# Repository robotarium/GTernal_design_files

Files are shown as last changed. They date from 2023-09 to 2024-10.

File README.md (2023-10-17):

# GTernal

If looking to purchase circuit boards, this link may hold an up to date CircuitHub order: https://circuithub.com/projects/Payday02/GTernal/revisions/51452/parts

Link to slightly older version with more testing: https://circuithub.com/projects/Payday02/Gritsbot-3/revisions/50001/parts

If looking for a BOM, it can be found in the Parts Folder or here on google sheets (Google sheets may likely be more up to date than the parts folder as parts go in and out of circulation) https://docs.google.com/spreadsheets/d/1fcbRilmKaX-AO9ylUm2N9gINN3ZsyIf4CjUE0T1iR2c/edit?usp=sharing

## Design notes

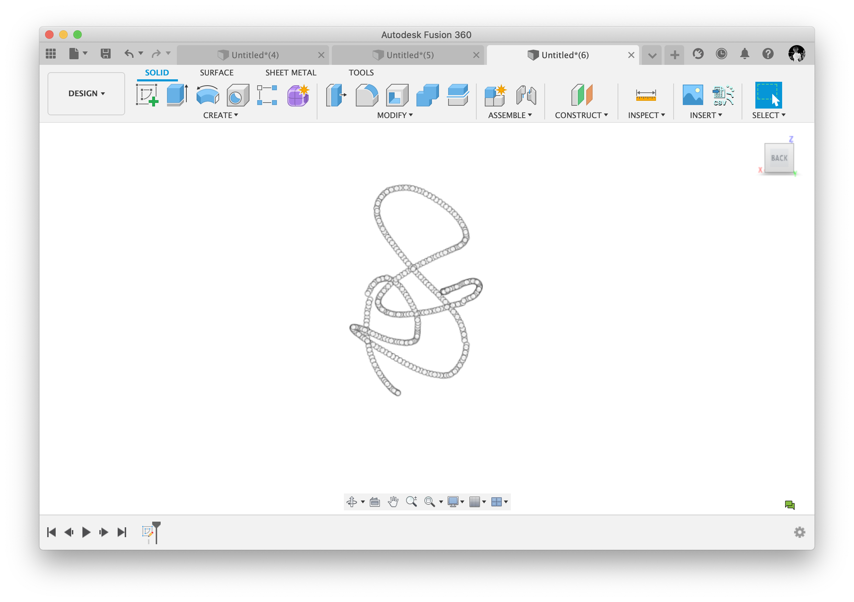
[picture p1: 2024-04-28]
Lasercutting_Files/GTernal_Top_Plates/ImportCSVPoints/images/sketcher_vr_Simple_back.png

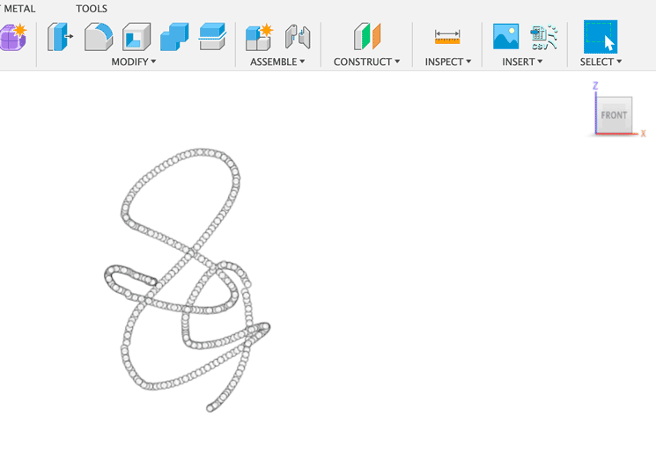
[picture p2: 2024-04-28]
Lasercutting_Files/GTernal_Top_Plates/ImportCSVPoints/images/sketcher_vr_Simple_anim.gif

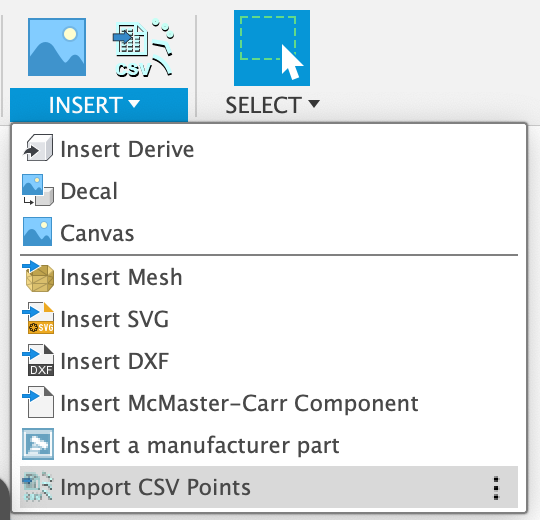
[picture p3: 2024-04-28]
Lasercutting_Files/GTernal_Top_Plates/ImportCSVPoints/images/insert-dropdown.png

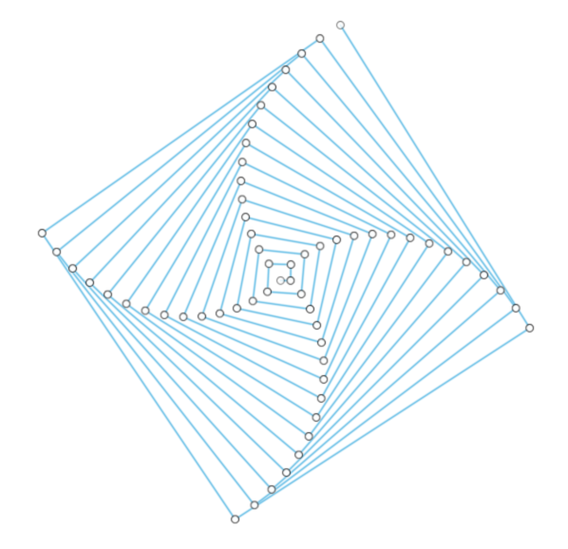
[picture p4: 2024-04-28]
Lasercutting_Files/GTernal_Top_Plates/ImportCSVPoints/images/spiralcube_sketch.png

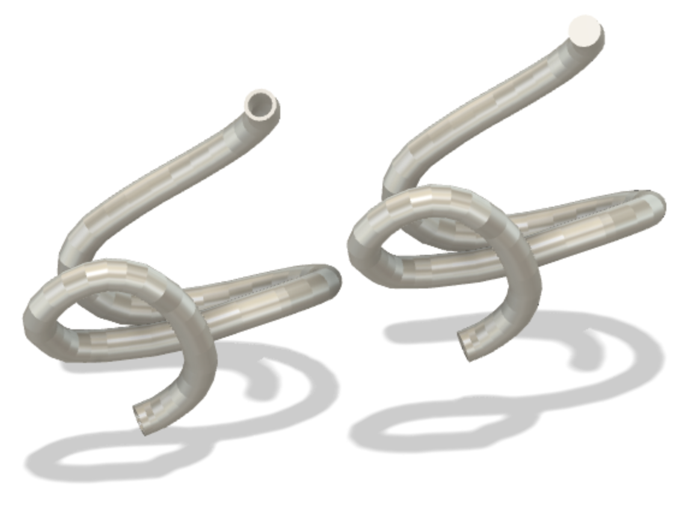
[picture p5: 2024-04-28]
Lasercutting_Files/GTernal_Top_Plates/ImportCSVPoints/images/sketcher_vr_Simple_pipes.png

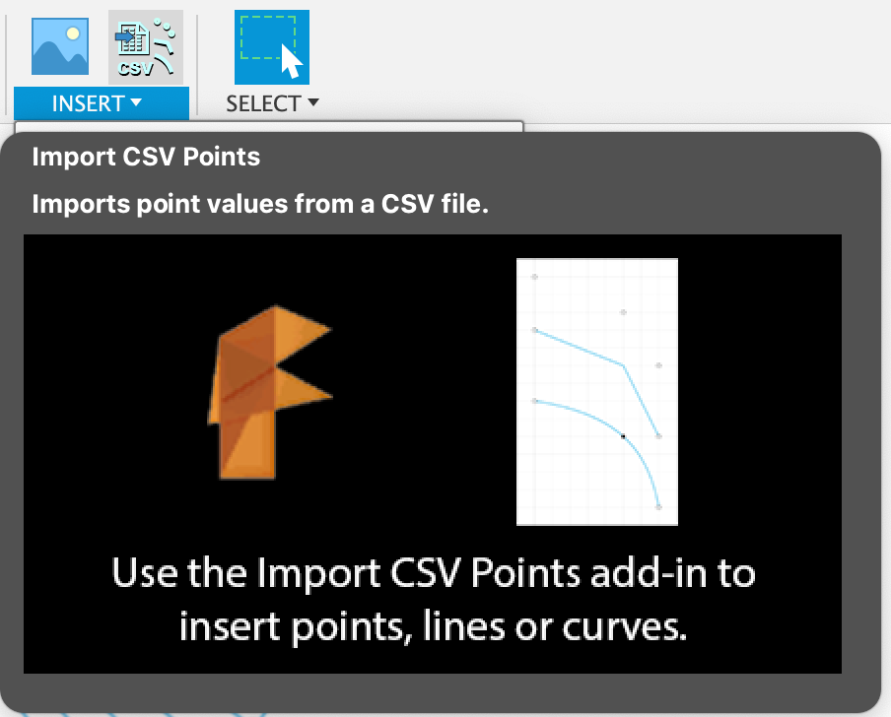
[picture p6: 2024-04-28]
Lasercutting_Files/GTernal_Top_Plates/ImportCSVPoints/images/insert-tooltip.png

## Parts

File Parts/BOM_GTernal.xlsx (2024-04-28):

Name | Link: | Quantity: | Price | Subtotal: | Use/Notes: | Parts Utilization Ratio
Nylon Standoffs (M2.5) | https://a.co/d/cnISycu | 11 | $14.99 | $164.89 | Only using 6 mm, 8 mm, and 20 mm. Pack comes with 15 of each and 4 of each are used per robot. | 0.9696969697
Qi Charger | https://a.co/d/bVD1k2u | 40 | $9.99 | $399.60 |  | 1
Micro SD Card (32 GB) | https://www.amazon.com/dp/B087JCL881/ref=twister_B08CLNX58K?_encoding=UTF8&th=1 | 20 | $15.89 | $317.80 | Pack of 2. 1 needed per robot | 1
Raspberry Pi Camera V2 | https://a.co/d/fKN2s0y | 40 | $19.99 | $799.60 |  | 1
Brass Standoffs (M2.5x15mm) | https://www.digikey.com/en/products/detail/assmann-wsw-components/V6622E/3511510 | 160 | $0.21 | $34.26 | 4 needed per robot | 1
Brass Standoffs (M2.5x10mm) | https://www.digikey.com/en/products/detail/assmann-wsw-components/V6622C/3511505 | 160 | $0.19 | $30.06 | 4 needed per robot | 1
M2.5x6mm Screw | https://www.mcmaster.com/90116A110/ | 2 | $11.10 | $22.20 | 4 Used per robot, pack of 100 | 0.8
Standoff Locknuts (M2.5) | https://www.mcmaster.com/93625A103/ | 7 | $7.00 | $49.00 | 4 Used per robot, pack of 25 | 0.9142857143
24"x24"x1/8" Acrylic sheet | https://www.mcmaster.com/product/8560K194 | 8 | $25.38 | $203.04 | Body Panels. About 5 robots per pannel | 1
12"x12"x1/16" Acrylic sheet | https://www.mcmaster.com/8560K171/ | 8 | $16.88 | $135.04 | Body Panels. About 5 robots per pannel | 1
M2.5x8mm Nylon Screws | https://www.mcmaster.com/92492A712-92492A658/ | 13 | $9.09 | $118.17 | Pack of 100. Distance sensors and Raspberry Pi Mounting. 32 screws per robot. | 0.9846153846
M2.5 Nuts | https://www.mcmaster.com/93800A350-93369A114/?s=m2.5+nylon+nut | 13 | $17.84 | $231.92 | Pack of 100. Distance sensors and Raspberry Pi Mounting. 32 screws per robot. | 0.9846153846
Caster Screws (M3x20mm) | https://www.mcmaster.com/92005A128/ | 2 | $5.14 | $10.28 | Pack of 100. 3 needed per robot | 0.6
Caster Lock Nuts (M3) | https://www.mcmaster.com/90576A102/ | 2 | $4.65 | $9.30 | Pack of 100. 3 needed per robot | 0.6
Pi Cam Screws (M2) | https://www.mcmaster.com/92492A704-92492A104/ | 2 | $13.77 | $27.54 | Pack of 100. 4 needed per robot. | 0.8
Pi Cam Nuts (M2) | https://www.mcmaster.com/93800A300/ | 2 | $20.13 | $40.26 | Pack of 100. 4 needed per robot. | 0.8
Vicon Marker Screws (4-40 1/2") | https://www.mcmaster.com/91772A110/ | 100 | $6.41 | $6.41 | Pack of 100 | NA
Vicon Marker Screws (4-40 3/4") | https://www.mcmaster.com/91772A113/ | 100 | $7.12 | $7.12 | Pack of 100 | NA
Vicon Marker Screws (4-40 1") | https://www.mcmaster.com/91772A115/ | 100 | $7.62 | $7.62 | Pack of 100 | NA
Vicon Marker Screws (4-40 1-1/4") | https://www.mcmaster.com/91772A116/ | 100 | $9.46 | $9.46 | Pack of 100 | NA
Vicon Marker Lock Nuts (4-40) | https://www.mcmaster.com/91831A005/ | 4 | $5.26 | $21.04 | Pack of 100 | NA
Raspberry Pi 4B (2GB) | https://www.sparkfun.com/products/15446 | 40 | 45 | 1800 |  | 1
JST 5-pin Connector | https://www.adafruit.com/product/4875 | 40 | $0.95 | $38.00 | Connector for PCB and RPi | 1
3.7v lipo Battery | https://www.adafruit.com/product/328 | 40 | $14.95 | $598.00 |  | 1
Distance Sensors | https://www.adafruit.com/product/5396 | 280 | $11.96 | $3348.80 | 7 Per robot | 1
Male Pin Header | https://www.adafruit.com/product/392 | 4 | $4.46 | $17.84 | Pack of 10 | 1
100:1 6v motor with encoder | https://www.digikey.com/en/products/detail/dfrobot/FIT0483/7087160?gad_source=1 | 80 | $11.50 | $920.00 | 2 Per robot | 1
Motor mount | https://www.digikey.com/en/products/detail/pololu-corporation/989/10449800 | 40 | $2.95 | $118.00 | Pack of 2. 2 needed per robot | 1
Wheel | https://www.digikey.com/en/products/detail/pololu-corporation/1087/10449804 | 40 | $3.95 | $158.00 | Pack of 2. 2 needed per robot | 1
Ball Caster | https://www.tamiyausa.com/shop/educational-construction/ball-caster-2pcs/ | 20 | $7 | $140.00 | Pack of 2. 1 needed per robot | 1
Caster Springs | https://www.mcmaster.com/9657K601/ | 10 | $6.93 | $69.30 | Pack of 12. 3 needed per robot | 1
Qwiic Cables Short | https://www.sparkfun.com/products/17260 | 280 | $0.95 | $266.00 | 7 needed per robot | 1
Teensy 4.0 | https://www.adafruit.com/product/4323 | 40 | $23.80 | $952.00 |  | 1
PCB | https://circuithub.com/projects/Payday02/GTernal/revisions/51452/parts | 40 | $123.87 | $4954.60 |  | 1
 |  |  | Total: | $16025.15
 | Number of Robots: | 40 | Total with 9% Tax: | $17467.41
 |  |  | Per Robot | $400.63
 |  |  | Per Robot w/ Tax | $436.69

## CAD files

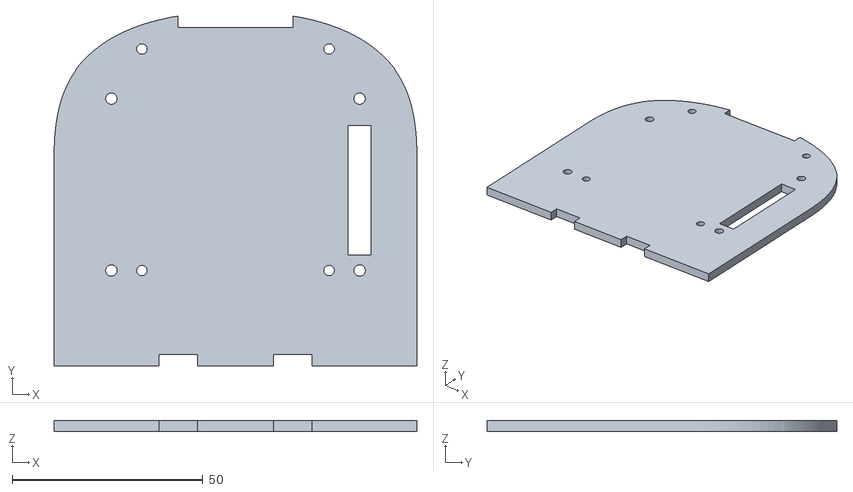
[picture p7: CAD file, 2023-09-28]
CAD_Files/OBJ Files/Top Main Plate.obj
95.0 x 91.6 x 3.00

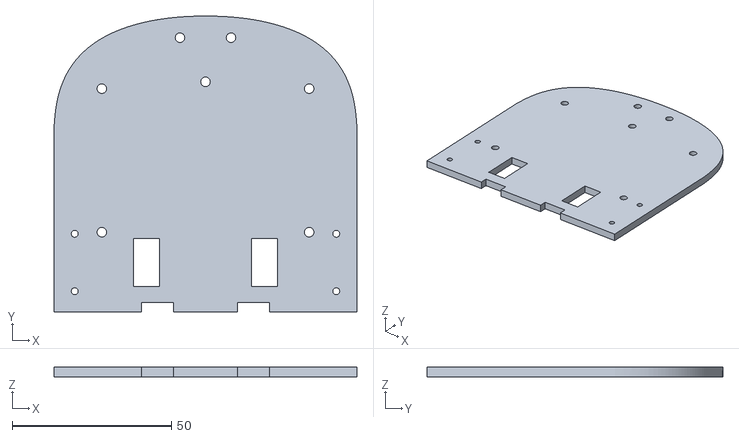
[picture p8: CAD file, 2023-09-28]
CAD_Files/OBJ Files/Bottom Panel.obj
95.0 x 92.8 x 3.00

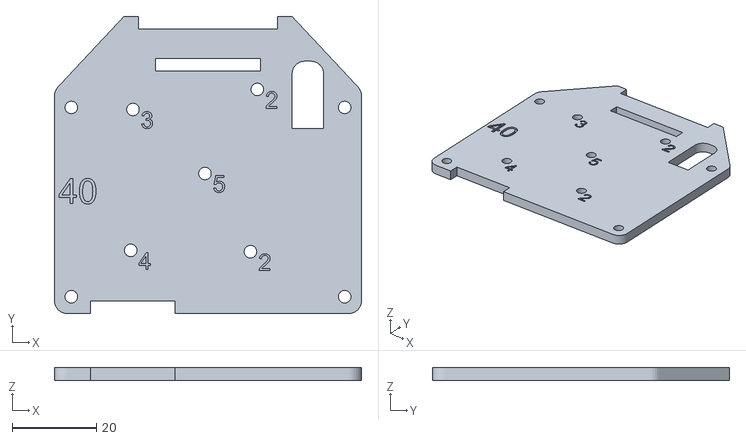
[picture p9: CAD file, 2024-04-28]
Lasercutting_Files/GTernal_Top_Plates/1-40 Objs/Body40.obj
73.0 x 70.6 x 3.00

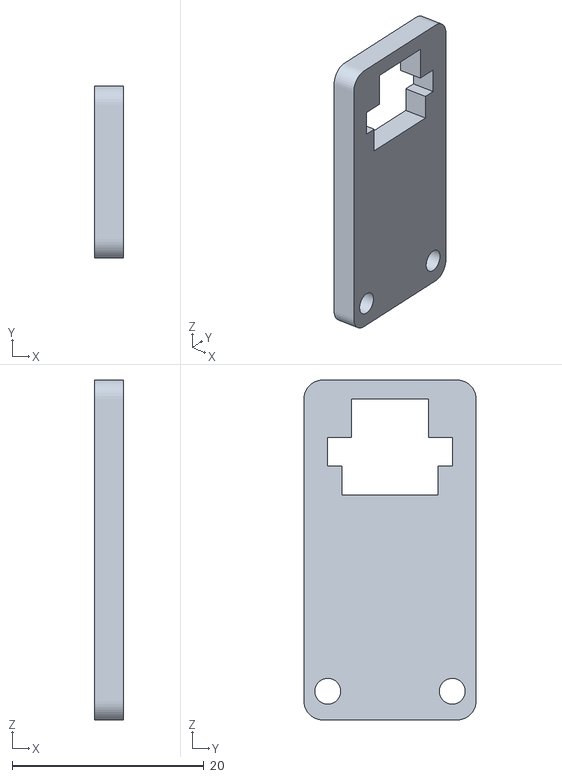
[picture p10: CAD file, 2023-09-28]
CAD_Files/OBJ Files/Distance Sensor Mount Subtractive Part 2 V5.obj
3.00 x 18.0 x 35.5

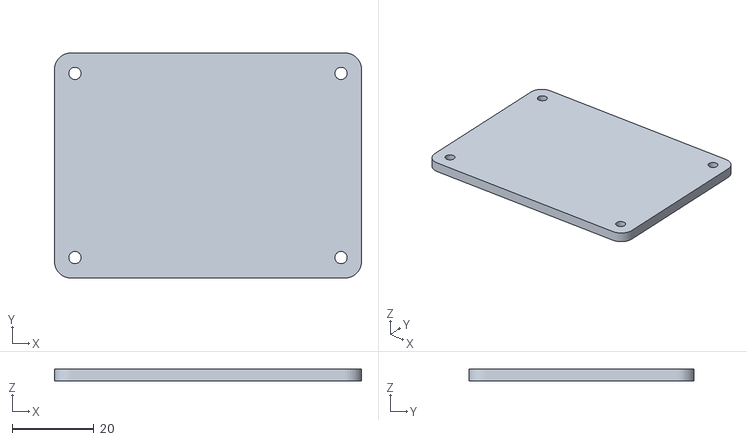
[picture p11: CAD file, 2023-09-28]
CAD_Files/OBJ Files/Battery Plate.obj
75.0 x 55.0 x 3.00

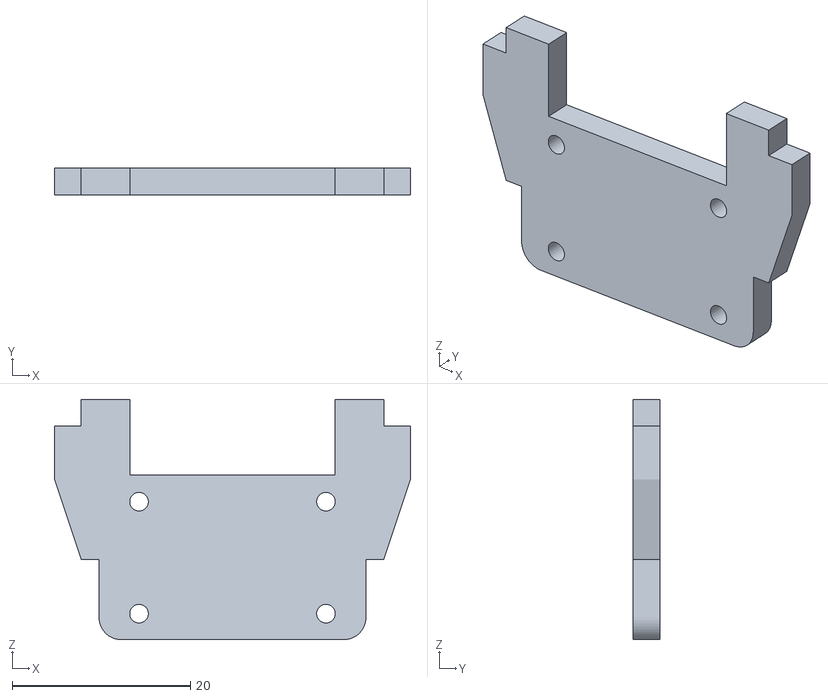
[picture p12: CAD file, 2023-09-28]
CAD_Files/OBJ Files/Camera Mount V3.obj
40.0 x 3.00 x 27.0

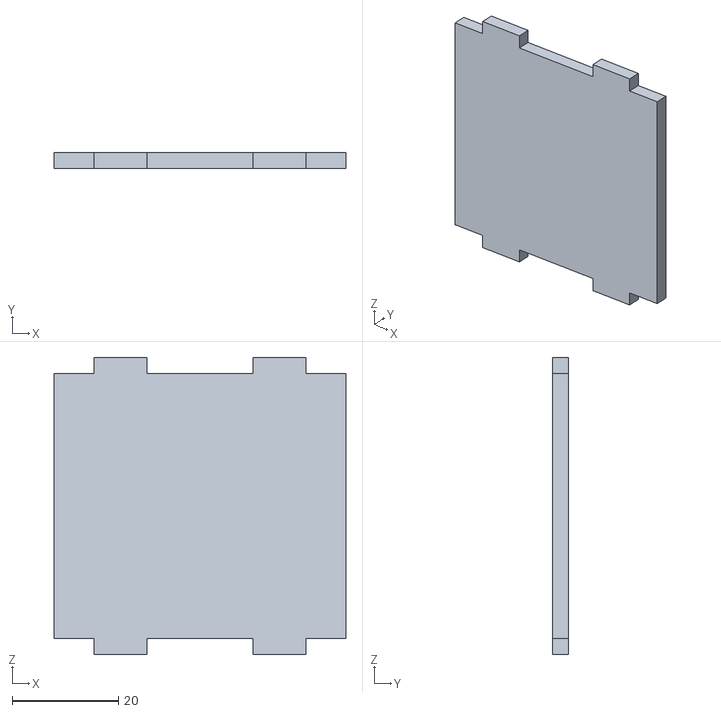
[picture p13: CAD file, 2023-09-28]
CAD_Files/OBJ Files/Back Panel 3mm.obj
55.0 x 3.00 x 56.0

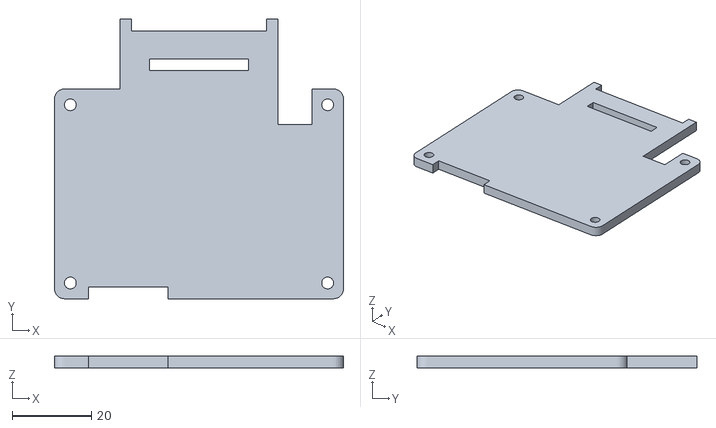
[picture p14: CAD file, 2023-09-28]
CAD_Files/OBJ Files/Top Plate V2.obj
73.0 x 70.6 x 3.00

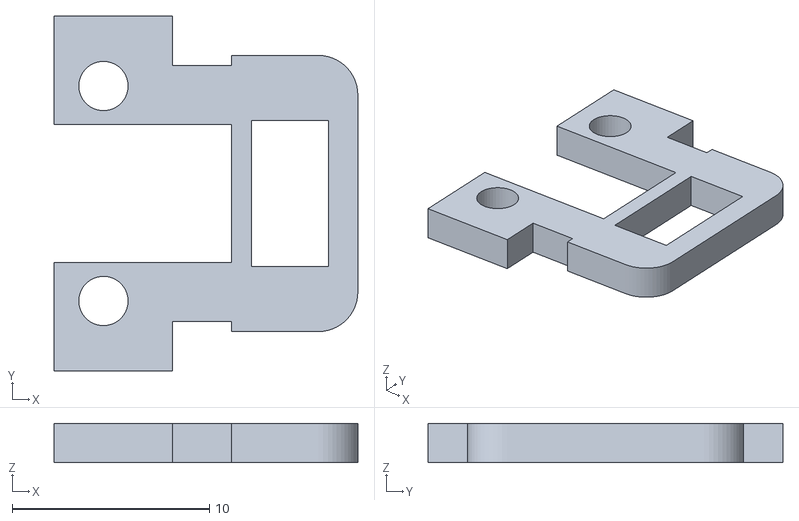
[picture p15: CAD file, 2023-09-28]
CAD_Files/OBJ Files/Distance Sensor mount sub part 1 V1.obj
15.4 x 18.0 x 2.00

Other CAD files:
Lasercutting_Files/GTernal_Top_Plates/1-40 Objs/Body22.obj
Lasercutting_Files/GTernal_Top_Plates/1-40 Objs/Body14.obj
Lasercutting_Files/GTernal_Top_Plates/1-40 Objs/Body2.obj
Lasercutting_Files/GTernal_Top_Plates/1-40 Objs/Body25.obj
Lasercutting_Files/GTernal_Top_Plates/1-40 Objs/Body1.obj
Lasercutting_Files/GTernal_Top_Plates/1-40 Objs/Body20.obj
Lasercutting_Files/GTernal_Top_Plates/1-40 Objs/Body28.obj
Lasercutting_Files/GTernal_Top_Plates/1-40 Objs/Body34.obj
Lasercutting_Files/GTernal_Top_Plates/1-40 Objs/Body19.obj
CAD_Files/Components/EDAC_1743_RJ45_TH.f3d
CAD_Files/Components/Pin+Header+2x2+TH+Pitch+2.f3d
CAD_Files/Components/SMD+PTC+Fuse+MF-MSMF250_16X.f3d
CAD_Files/Components/SOP-3+2.f3d
CAD_Files/Components/SOP-3.f3d
CAD_Files/Components/TSOP-2+4mm.f3d
CAD_Files/Components/TSOP-6+2mm.f3d
CAD_Files/Components/TSOP-6+3mm (1).f3d
CAD_Files/Components/TSOP-6+3mm.f3d
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

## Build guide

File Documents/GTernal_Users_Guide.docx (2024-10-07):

GTernal 1.1

User’s Guide

Paden Davis, Maxwell Chen, Nathan Yam,

Soobum Kim, Sean Wilson, Samuel Coogan

October, 2024

Table of Contents

# 1 Purpose

The purpose of this document is to explain the general design elements, assembly, and usage of the GTernal 1.1 robot.

# 2 Printed Circuit Board (PCB)

The printed circuit board (PCB) houses most of the electronics on the robot and features circuitry for power and sensors. Some of the circuitry is taken from the GRITSBot 2.0 PCB while other components are copied and modified versions of circuitry from breakout boards.

The top side of the PCB includes an On/Off switch, status LEDs, and an area for mounting a Teensy 4.0 microcontroller.

This section will detail the core components of the GTernal 1.0 PCB.

## 2.1 On/Off Switch

The On/Off switch turns on and off the 5V and 6V power circuits of the robot. The On/Off switch has no connection to the charging circuitry.

## 2.2 Status LEDs

Status LED | Description
PWR | On when On/Off switch is on and receiving power from battery/charger
LBO | Low battery indicator
CHRG | On when battery is charging or only charger connected.
DONE | On when batter is done charging.

## 2.3 5V Regulation

The 5V Regulation circuitry is taken and modified from Adafruit’s PowerBoost 1000C board (https://www.adafruit.com/product/2465).

The circuitry takes power from the battery/charger and regulates it to 5V to power the Teensy, motor encoders, and motor driver.

## 2.4 6V Regulation

The 6V Regulation circuitry is taken from the GRITSBot 2.0 PCB.

The circuitry takes power from the battery/charger and regulates it to 6V for motor power.

## 2.5 Charging Circuitry

The charging circuitry is taken and modified from Adafruit’s PowerBoost 1000C board (https://www.adafruit.com/product/2465).

The circuitry handles charging the robot battery and load-sharing between charger and battery.

## 2.6 Power Sensor

The power monitor is taken and modified from Adafruit’s INA260 Breakout Board (https://www.adafruit.com/product/4226).

The INA260 power sensor is wired in series with the VBAT line directly after the charging circuitry and measures VBAT voltage/current and power usage.

If undesired, the PCB features pads for a jumper on the VBAT line to bypass the power sensor.

## 2.7 Teensy 4.0

The Teensy 4.0 (https://www.pjrc.com/store/teensy40.html) is a low-level microcontroller board that handles sensor and motor driver communications and control.

The Teensy takes in 5V and provides 3.3V for sensor power. The Teensy can be connected to microUSB for programming.

WARNING: There is potential for damage to the 5V regulation circuitry if the Teensy is connected to microUSB without battery/charger power. The cause is unknown at the moment but may be due to pre-biasing the output of the TPS61030 chip. Ensure that the robot is fully powered through battery/charger first before connecting the Teensy with microUSB that has external power.

## 2.8 H-Bridge Motor Driver

The H-Bridge Motor Driver takes power from 5V regulation and uses 6V for motor power. The driver is controlled by the Teensy.

## 2.9 I²C Mux and Qwiic Connectors

The I²C is taken and modified from Sparkfun’s Qwiic Mux Breakout (https://www.sparkfun.com/products/16784).

The GTernal 1.0 features seven distance sensors (https://www.adafruit.com/product/3317) with the same, unmodifiable I²C address, so I²C mux circuitry is needed to properly access all of them.

The GTernal 1.0 PCB includes Qwiic connectors for wiring to the distance sensors and holes for distance sensor mounts.

## 2.10 Inertial Measurement Unit (IMU)

The I²C is taken and modified from Adafruit’s BNO055 Breakout Board (https://www.adafruit.com/product/2472).

## 2.10 Pi Power & Communication

The PCB features 4 pins for providing power and serial communication to a Raspberry Pi.

# 3 Other Electronics and Components

This section details other electronics and components not on the PCB.

## 3.1 Distance Sensors

The GTernal 1.0 features seven Adafruit VL53L0X Time of Flight Distance Sensors (https://www.adafruit.com/product/3317).

These distance sensors are connected to the PCB through a Qwiic cable and should be held using 3D-printed or laser-cut mounts that can be bolted to the PCB.

## 3.2 Raspberry Pi

The GTernal 1.0 supports Raspberry Pi 3, 3b, 3b+, and 4.

The Raspberry Pi receives power from the Pi power pins on the PCB.

The Raspberry Pi serves as the main processor for the robot and communicates with the Teensy either through serial pins on the PCB or through USB

## 3.3 Pi Camera

The intended camera is a Raspberry Pi Camera V2 (https://www.raspberrypi.com/products/camera-module-v2/), but the GTernal 1.1 should support any camera that connects to a Raspberry Pi through the CSI connector.

## 3.4 Motors

The GTernal 1.0 uses two geared motors with encoders from DFRobot (https://www.dfrobot.com/product-1433.html).

## 3.5 Battery

The GTernal 1.0 uses a 3.7V LiPo Battery from Adafruit (https://www.adafruit.com/product/328)

# 4 Assembly

This section’s purpose is to walk through the steps involved in putting together a working robot once all of the parts have been purchased or manufactured. To this end, the assembly process will require:

- 1x GTernal 1.0 assembled printed circuit board (PCB)
- 1x Set of cut acrylic pieces (see 4.1)
  - Bottom plate
  - Pi mount plate
  - Top plate
  - Battery plates
  - 2x Back plates
  - 7x Distance sensor mount plates
  - Camera mount plate
- 1x 3.7V LiPo Battery
- 1x Teensy 4.0 board with pins soldered
- 1x Raspberry Pi (3B, 3B+, 4)
- 1x JST SH Jumper Wire
- 7x Time of Flight (ToF) distance sensors
- 7x 50mm or shorter Qwiic connector cables
- 1x Front Caster Pack
- 3x Small Caster Springs
- 3x M3x20mm Screws
- 3x M3 Locknuts
- 2x 100:1 Motors
- 1x Pack of two motor mounts
- 1x Pack of two wheels
- 4x M2.5x15mm brass male to female standoffs
- 4x M2.5x10mm brass male to female standoffs
- 4x M2.5x6mm nylon male to female standoffs
- 4x M2.5x10mm nylon male to female standoffs
- 4x M2.5x20mm nylon male to female standoffs
- 4x M2.5 Locknuts
- 4x M2.5x6mm Screws
- 14x M2 nylon Screws
- 14x M2 nylon Nuts

## 4.1 Cut Acrylic Pieces

.svg and .pdf files for laser cutting acrylic pieces can be found in the GTernal GitHub repository under “GTernal/Lasercutting Files”.

Piece label is given inside square brackets.

Images in this section are not to scale.

### 4.1.1 Bottom Plate [A1]

Thickness: 1/8” (3 mm)

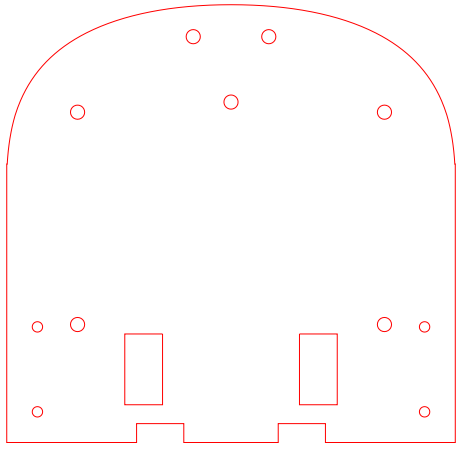
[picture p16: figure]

### 4.1.2 Pi Mount Plate [A2]

Thickness: 1/8” (3 mm)

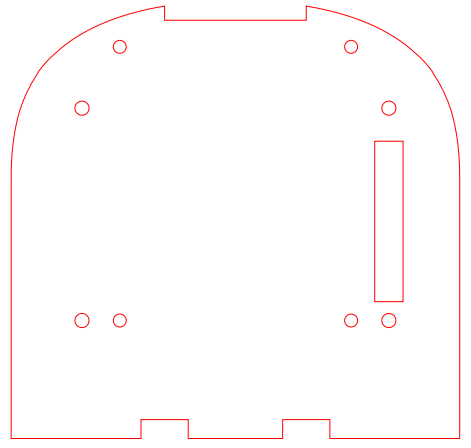
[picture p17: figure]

### 4.1.3 Top Plate [A3]

Thickness: 1/16” (1.5 mm)
Left: base top plate.
Right: example top plate with holes for mounting Vicon trackers

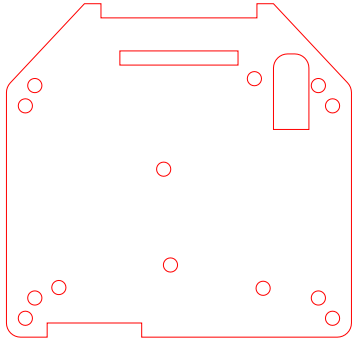
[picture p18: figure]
A red outline of a machine

### 4.1.4 Battery Plates [A4b, A4t]

Bottom Plate [A4b] Thickness: 1/8” (3 mm)

Top Plate [A4t] Thickness: 1/16” (1.5 mm)

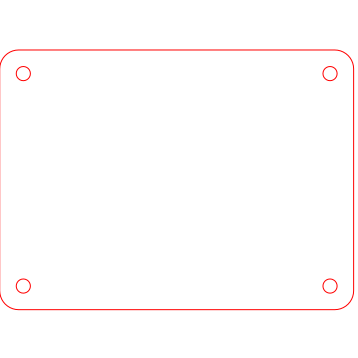
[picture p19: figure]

### 4.1.5 Back Plates [A5]

Thickness: 1/16” (1.5 mm)

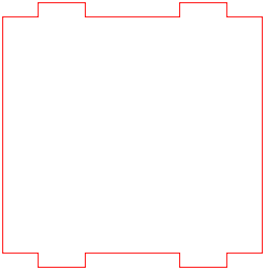
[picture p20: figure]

### 4.1.6 Distance Sensor Mount Plates [A6a, A6b]

Thickness: 1/8” (3 mm)

Number: 7x

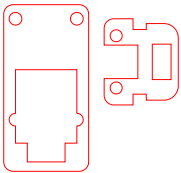
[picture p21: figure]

### 4.1.7 Camera Mount Plate [A7]

Thickness: 1/8” (3 mm)

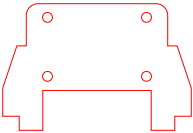
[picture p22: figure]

## 4.2 Assembly with an Assembled Circuit Board

For this process, the steps are much simpler than without a circuit board (PCB), as all connections except the motor connections will involve no soldering.

1. Mount the teensy onto the top of the PCB by putting the pins through the holes in the marked section on the silkscreen then soldering the pins to the PCB.
2. Solder the motor connectors that come with each motor into the holes marked motorR and motorL respectively. Review pinouts for the motor, motor cable, and PCB to ensure correct connection.
3. The distance sensor mounts are made of two acrylic plates [A6a] and [A6b].
  i. Take the smaller plate [A6b] and insert it diagonally through the center hole of the larger plate [A6a].
  ii. Rotate and shift [A6b] until it snaps into place horizontally near the edge of plate [A6a].

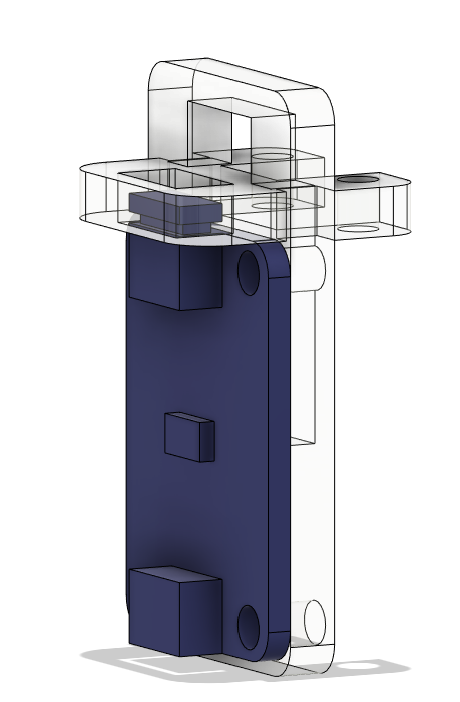
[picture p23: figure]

4. Repeat step (3) six more times to obtain seven total distance sensor mounts.
5. Mounting a distance sensor onto a distance sensor mount.
  i. Take a 50mm or shorter Qwiic connector cable and plug it into the connector on the side with the LED. When facing distance sensor with top silkscreen text upright, this is the left connector.
  ii. Thread the Qwiic connector cable through the upper donut hole in piece A6a in the distance sensor mount.
  iii. With the cable through the hole, align the right-side distance sensor holes with the bottom holes on the larger plate [A6a] of the distance sensor mount.
  iv. Secure the distance sensor using 2x M2x8mm nylon screws and 2x M2 nylon nuts on the bottom holes of the distance sensor mount.
6. Repeat step (5) six more times to obtain seven total mounted distance sensors with Qwiic jumpers out the back of the mount.
7. Mounting distance sensors to PCB
  i. With the Qwiic connector cable plugged into the distance sensor, plug the free connector on the cable into the Qwiic connector on the PCB.
  ii. Using 2x M2x8mm nylon screws and 2x M2 nylon nuts, secure the distance sensor mount into the PCB through the screw holes on acrylic piece [A6b].
8. Repeat step (7) for all seven distance sensors. Set the PCB to the side gently once all seven are mounted.
9. Begin with the bottom acrylic plate [A1]. This one has two rectangular holes near the bottom side and three screw holes in the front. Screw 4 M2.5x10mm brass standoffs into lock nuts through the four rectangularly spaced holes in the plate. Use pliers to hold them while screwing into the locknut if necessary.
10. Place the motors into their mounting brackets, making sure the flat panel at the end of the gearbox lines up with the edge of the bracket. Mount the brackets and motors to the bottom side (opposite side to the standoffs) of the acrylic plate [A1] using the screws provided with the brackets.

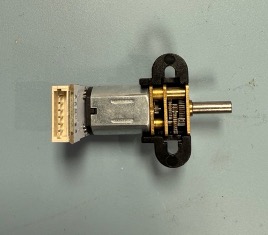
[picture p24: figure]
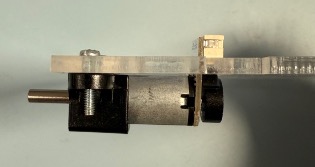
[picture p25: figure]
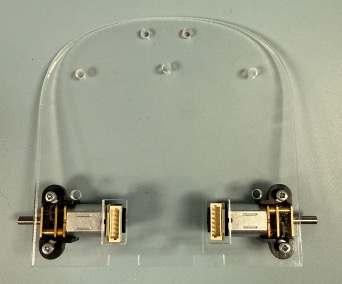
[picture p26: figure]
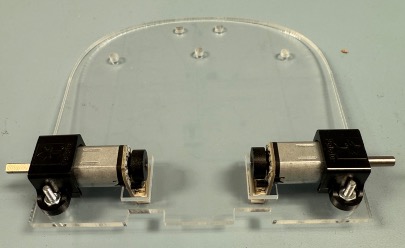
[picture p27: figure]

11. Place the wheels onto the motor shafts and make sure the wheels are angled straight and do not rub against the acrylic. Place the rubber ring on the outside to tighten them and lock them in place.
12. Mounting the caster wheel to the bottom plate [A1].
  i. Clip the caster wheel components out of the injection molded sprue. Set aside the mounting base since it will not be used.
  ii. Place the metal marble in the bottom holder.
  iii. Place three metal pins on top of the ball in each of the edge locations.

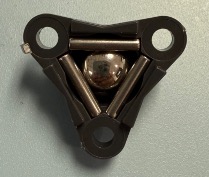
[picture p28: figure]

  iv. Place the top onto the caster assembly.
  v. Thread 3x M3x20mm screws into the three holes on the caster.
  vi. Place the caster springs and the 2mm spacers that come with the casters onto the screws.
  vii. Carefully slot all three screws through the holes in the front of the bottom plate [A1]. Secure the screws in place with 3x M3 Locknuts.

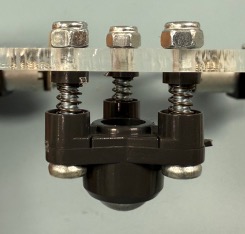
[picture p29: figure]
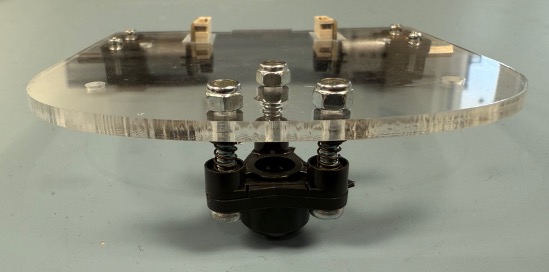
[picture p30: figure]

  viii. Check if the bottom plate is level. Adjust the 3x M3 Locknuts if necessary.

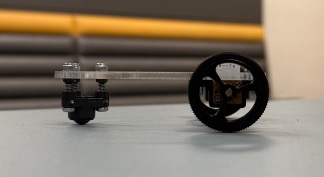
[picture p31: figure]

13. Place the bottom battery plate [A4b] (rectangle with rounded corners) onto the standoffs and attach 4x 10mm nylon standoffs through it into the brass standoffs of the bottom plate [A1] to secure it in place.
14. On top of the bottom battery plate [A4b], place the battery.
15. With the top battery plate [A4t] close, take the battery wires and place them under the plate [A4t] in a way that will hold them and leaves about 2cm of wire free.
16. Press the top battery plate [A4t] down and attach 4x 6mm nylon standoffs to secure it in place.
17. Mounting the PCB
  i. Ensure the power switch is switched off (towards the bottom of the board).
  ii. Bring the PCB with the teensy attached close.
  iii. Route the motor wires under the PCB (careful to go around the teensy pins) and across each other.
  iv. Place the PCB on the standoffs and secure it with 4x 20mm standoffs.
  v. Plug the motor connectors into their corresponding motor
  vi. Plug the battery cable into the battery connector. All lights should be off if the switch is in the off position.
18. Place the JST SH connector into the Pi Communication connector on the PCB
19. Screw the Raspberry Pi onto the Pi mount plate [A2], which looks similar to the bottom plate of the robot, using 4x M2x8mm nylon screws and nuts.
20. Thread the four wires through the slot on the right side of the plate and connect them to pins 2,3,4,5 (5v, GND, Tx, Rx) from the top on the right column of pins in the same order they are on the PCB.
21. Attach the Pi mount plate [A2] to the standoffs from the PCB using 4x M2.5x15mm brass standoffs.
22. If using Vicon Trackers, attach the screws used for the tracking balls into the top plate
23. Securing the top plate [A3]
  i. If using the camera, route the camera cable through the plate and into the connector on the Pi before screwing the plate in
  ii. Screw on the top plate [A3] using 4x M2.5x6mm screws.
24. If using the camera, press fit the camera mount plate into the front slots. Then mount the camera to the camera mount plate.
25. Backplates and Qi Charger
  i. Press fit one back plate [A5] into the grooves
  ii. Plug the Qi Charger into the charging microUSB port on the side of the PCB
  iii. Place the flat side against the back plate [A5] that was mounted in step (25i).
  iv. Place another back plate [A5] into the same grooves, sandwiching the Qi charger between two plates to hold it in place.

# 5 Uploading Code and Using the GTernal 1.0

Upload the Teensy code found in the GitHub Gritsbot3/Firmware/teensyCode folder into the Teensy on the PCB through its microUSB port. Remember to have the board powered on and connected to the battery or charge port before plugging in the Teensy. This will require the Gritsbot3/Library folder to be placed in your Arduino libraries and the Arduino IDE set up to work with Teensy 4.0 which can be done following this guide (https://www.pjrc.com/teensy/td_download.html).

Image the Raspberry Pi SD card with the image provided in the GitHub repository and plug that into the Pi. Power the Pi by turning on the GTernal robot and connect the Pi to a monitor through the HDMI port or USB C port depending on which version you are using. Plug a mouse and keyboard into the rear USB A ports and use this to complete the setup of the Pi and add a Wi-Fi connection. A Wi-Fi antenna can optionally be connected into the rear USB A ports for better signal.

# 6 Future Changes

- Add additional pinout headers to the PCB or a Qwiic header to allow extra I2C connections for breakout boards.
- Mosfet for cutting power to the Pi for charging timeouts
- Move PCB components to improve ground/power connections and heat characteristics.

# 7 Links and References

## 7.1 Bill of Materials

GTernal 1.0 BOM: https://docs.google.com/spreadsheets/d/1fcbRilmKaX-AO9ylUm2N9gINN3ZsyIf4CjUE0T1iR2c/edit?usp=sharing

## 7.2 GitHub

GTernal 1.0: https://github.com/robotarium/GTernal

GRITSBot 2.0 Hardware: https://github.com/robotarium/GRITSBot_hardware_design

## 7.3 Robotarium

Robotarium at Georgia Tech: https://www.robotarium.gatech.edu/

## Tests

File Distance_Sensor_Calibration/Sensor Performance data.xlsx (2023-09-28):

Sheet: Export Summary
This document was exported from Numbers. Each table was converted to an Excel worksheet. All other objects on each Numbers sheet were placed on separate worksheets. Please be aware that formula calculations may differ in Excel.
Numbers Sheet Name | Numbers Table Name | Excel Worksheet Name
20 inches
 | Table 1 | 20 inches
12 inches
 | Table 1 | 12 inches
4 inches
 | Table 1 | 4 inches
3 inches
 | Table 1 | 3 inches
2 inches
 | Table 1 | 2 inches
6 inches
 | Table 1 | 6 inches
8 inches
 | Table 1 | 8 inches
10 inches
 | Table 1 | 10 inches
14 inches
 | Table 1 | 14 inches
16 inches
 | Table 1 | 16 inches
18 inches
 | Table 1 | 18 inches
22 inches
 | Table 1 | 22 inches
24 inches
 | Table 1 | 24 inches
26 inches
 | Table 1 | 26 inches
28 inches
 | Table 1 | 28 inches
Sheet 4
 | Table 1 | Sheet 4
Sheet 1
 | Table 1 | Sheet 1
Graphs
 | Table 1 | Graphs
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

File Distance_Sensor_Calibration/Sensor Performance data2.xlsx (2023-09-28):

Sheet: Export Summary
This document was exported from Numbers. Each table was converted to an Excel worksheet. All other objects on each Numbers sheet were placed on separate worksheets. Please be aware that formula calculations may differ in Excel.
Numbers Sheet Name | Numbers Table Name | Excel Worksheet Name
20 inches
 | Table 1 | 20 inches
12 inches
 | Table 1 | 12 inches
4 inches
 | Table 1 | 4 inches
3 inches
 | Table 1 | 3 inches
2 inches
 | Table 1 | 2 inches
6 inches
 | Table 1 | 6 inches
8 inches
 | Table 1 | 8 inches
10 inches
 | Table 1 | 10 inches
14 inches
 | Table 1 | 14 inches
16 inches
 | Table 1 | 16 inches
18 inches
 | Table 1 | 18 inches
22 inches
 | Table 1 | 22 inches
24 inches
 | Table 1 | 24 inches
26 inches
 | Table 1 | 26 inches
28 inches
 | Table 1 | 28 inches
Graphs
 | Table 1 | Graphs
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

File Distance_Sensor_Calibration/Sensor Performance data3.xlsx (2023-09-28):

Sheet: Export Summary
This document was exported from Numbers. Each table was converted to an Excel worksheet. All other objects on each Numbers sheet were placed on separate worksheets. Please be aware that formula calculations may differ in Excel.
Numbers Sheet Name | Numbers Table Name | Excel Worksheet Name
20 inches
 | Table 1 | 20 inches
12 inches
 | Table 1 | 12 inches
4 inches
 | Table 1 | 4 inches
3 inches
 | Table 1 | 3 inches
2 inches
 | Table 1 | 2 inches
6 inches
 | Table 1 | 6 inches
8 inches
 | Table 1 | 8 inches
10 inches
 | Table 1 | 10 inches
14 inches
 | Table 1 | 14 inches
16 inches
 | Table 1 | 16 inches
18 inches
 | Table 1 | 18 inches
22 inches
 | Table 1 | 22 inches
24 inches
 | Table 1 | 24 inches
26 inches
 | Table 1 | 26 inches
28 inches
 | Table 1 | 28 inches
Graphs
 | Table 1 | Graphs
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

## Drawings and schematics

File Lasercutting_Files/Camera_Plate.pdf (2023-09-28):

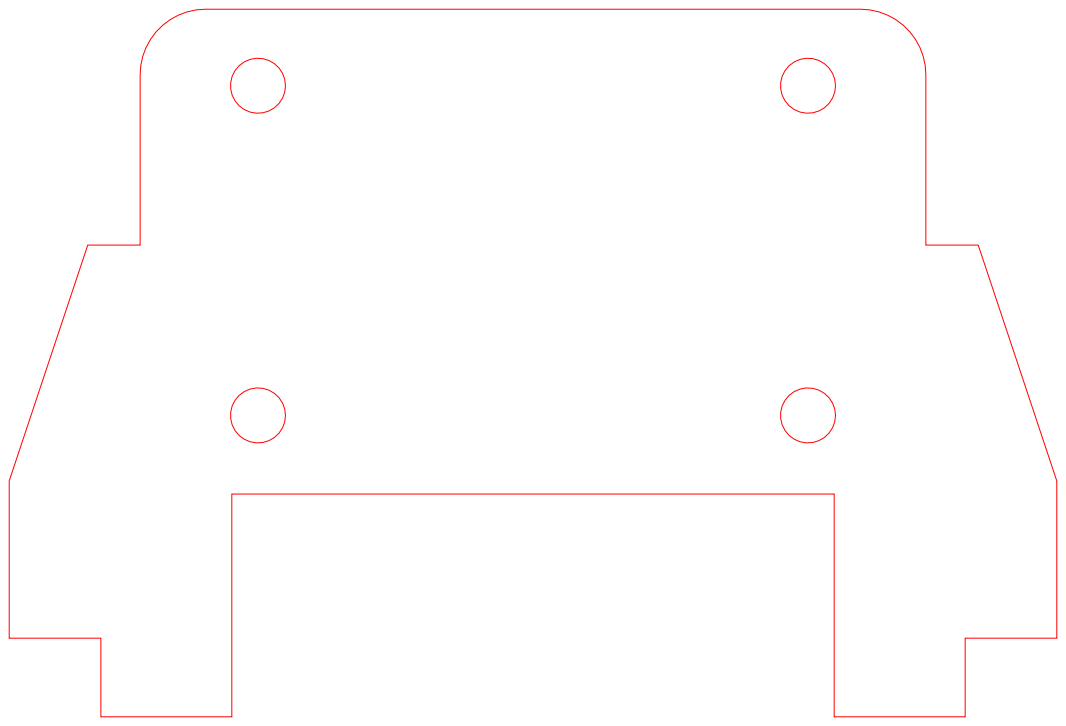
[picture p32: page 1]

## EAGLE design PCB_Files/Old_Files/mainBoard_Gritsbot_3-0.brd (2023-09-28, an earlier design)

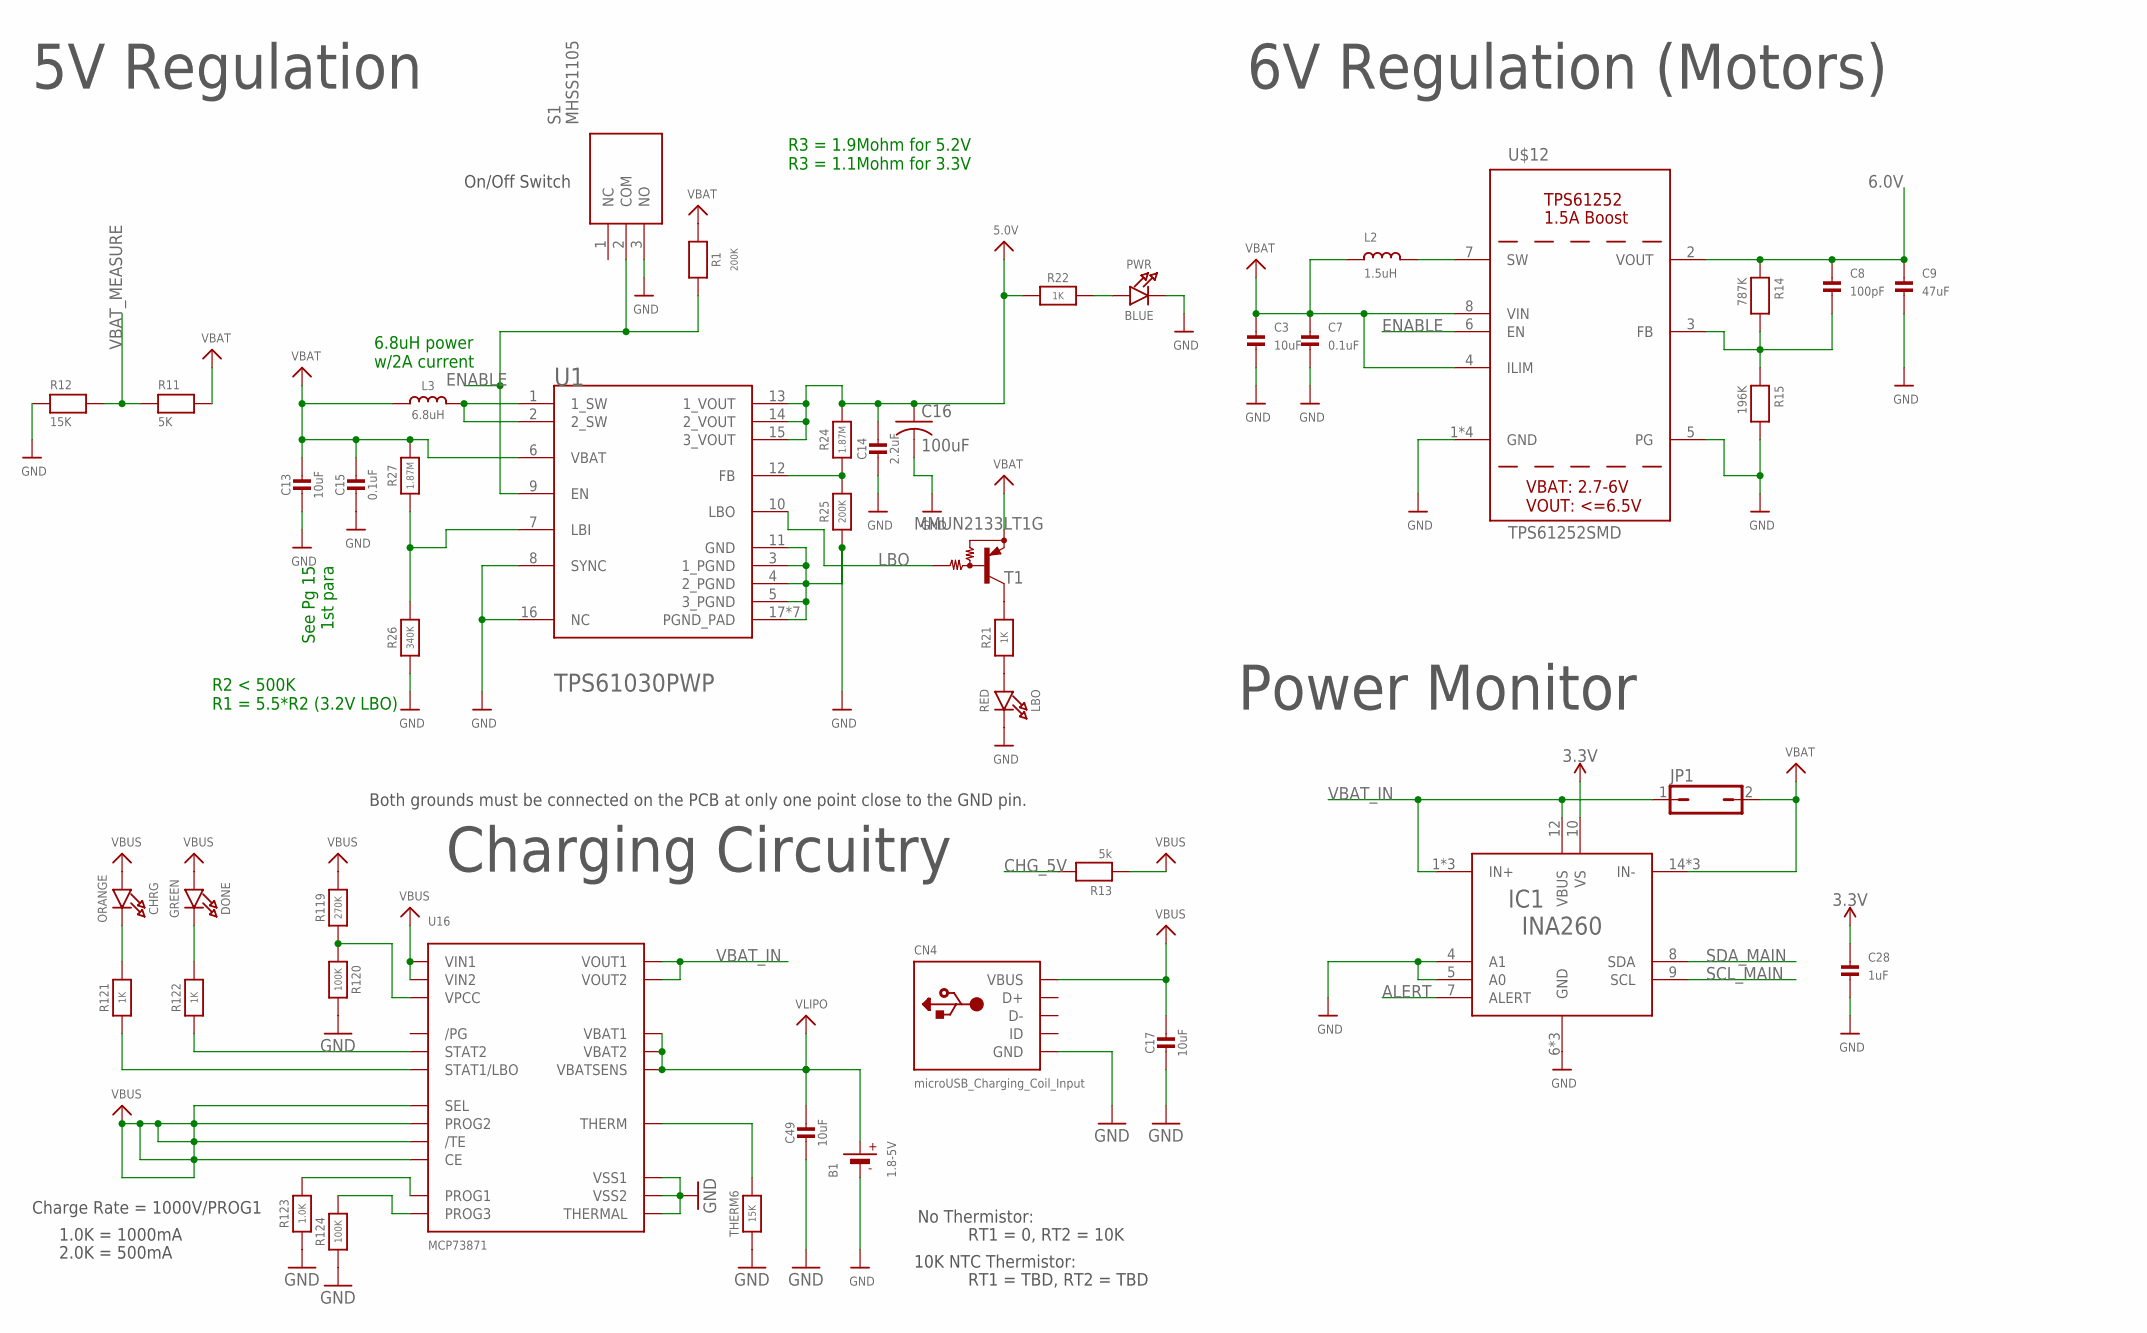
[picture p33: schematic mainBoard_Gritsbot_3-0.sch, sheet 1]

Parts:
B1: 1.8-5V; JSTPH2
C3: 10uF; 0603
C7: 0.1uF; 0805
C8: 100pF; 0603
C9: 47uF; 1206
C13, C17, C49: 10uF; 0805-NO
C14: 2.2uF; 0805-NO
C15: 0.1uF; 0805_10MGAP
C16: 100uF; C1210
C28: 1uF; 0603-NO
CHRG: ORANGE; CHIPLED_0805_NOOUTLINE
CN4: microUSB_Charging_Coil_Input; 4UCONN_20329
DONE: GREEN; CHIPLED_0805_NOOUTLINE
IC1: INA260; TSSOP16
JP1: JP1Q; JP1
L2: 1.5uH; MURATA_DFE252012P-1R5M=P2
L3: 6.8uH; INDUCTOR_5X5MM_TDK_VLC5045
LBO: RED; CHIPLED_0805_NOOUTLINE
PWR: BLUE; CHIPLED_0805_NOOUTLINE
R1, R25: 200K; 0805-NO
R11: 5K; 0805
R12: 15K; 0805
R13: 5k; 0805
R14: 787K; 0805
R15: 196K; 0805
R21, R22, R121, R122: 1K; 0805-NO
R24: 1.87M; 0805-NO
R26: 340K; _0805MP
R27: 1.87M; _0805MP
R119: 270K; 0805-NO
R120, R124: 100K; 0805-NO
R123: 1.0K; 0805-NO
S1: MHSS1105
T1: MMUN2133LT1G; SC59-BEC
THERM6: 15K; 0805-NO
U1: TEXAS_INSTRUMENTS_TPS61030PWPTEXAS_INSTRUMENTS_TP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; TEXAS_INSTRUMENTS_TPS61030PWP_0
U16: MCP73871; QFN20_4MM
U$12: TPS61252SMD; TPS61252

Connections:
3.3V: C28.1, IC1.10 (VS); also elsewhere on the board
5.0V: C14.1, C16.1, R22.1, R24.2, U1.13 (1_VOUT), U1.14 (2_VOUT), U1.15 (3_VOUT); also elsewhere on the board
6.0V: C8.1, C9.1, R14.1, U$12.2 (VOUT); also elsewhere on the board
ALERT: IC1.7 (ALERT)
CHG_5V: R13.2; also elsewhere on the board
ENABLE: R1.2, S1.2 (COM), U1.9 (EN), U$12.6 (EN)
GND: B1.1 (-), C3.2, C7.2, C9.2, C13.2, C14.2, C15.2, C16.2, C17.2, C28.2, C49.2, CN4.BASE@1 (GND), CN4.BASE@2 (GND), CN4.GND, CN4.SPRT@1 (GND), CN4.SPRT@2 (GND), CN4.SPRT@3 (GND), CN4.SPRT@4 (GND), IC1.4 (A1), IC1.5 (A0), IC1.6 (GND), IC1.11 (GND), IC1.13 (GND), LBO.C, PWR.C, R12.1, R15.2, R25.1, R26.1, R120.2, R123.1, R124.1, S1.3 (NO), THERM6.1, U1.3 (1_PGND), U1.4 (2_PGND), U1.5 (3_PGND), U1.8 (SYNC), U1.11 (GND), U1.16 (NC), U1.17 (PGND_PAD), U1.PAD_1 (PGND_PAD), U1.PAD_2 (PGND_PAD), U1.PAD_3 (PGND_PAD), U1.PAD_4 (PGND_PAD), U1.PAD_5 (PGND_PAD), U1.PAD_6 (PGND_PAD), U16.P$10 (VSS1), U16.P$11 (VSS2), U16.P$21 (THERMAL), U$12.1 (GND), U$12.5 (PG), U$12.P$2_GND (GND), U$12.P$3_GND (GND), U$12.THERMAL_GND (GND); also elsewhere on the board
LBO: T1.B, U1.10 (LBO)
unnamed: R24.1, R25.2, U1.12 (FB)
unnamed: L2.P$2 (2), U$12.7 (SW)
unnamed: C8.2, R14.2, R15.1, U$12.3 (FB)
unnamed: L3.P$2 (2), U1.1 (1_SW), U1.2 (2_SW)
unnamed: R26.2, R27.1, U1.7 (LBI)
unnamed: LBO.A, R21.1
unnamed: R21.2, T1.C
unnamed: PWR.A, R22.2
unnamed: R119.1, R120.1, U16.P$2 (VPCC)
unnamed: R122.1, U16.P$7 (STAT2)
unnamed: R121.1, U16.P$8 (STAT1/LBO)
unnamed: R123.2, U16.P$13 (PROG1)
unnamed: THERM6.2, U16.P$5 (THERM)
unnamed: DONE.C, R122.2
unnamed: CHRG.C, R121.2
unnamed: R124.2, U16.P$12 (PROG3)
SCL_MAIN: IC1.9 (SCL); also elsewhere on the board
SDA_MAIN: IC1.8 (SDA); also elsewhere on the board
VBAT: C3.1, C7.1, C13.1, C15.1, IC1.14 (IN-), IC1.15 (IN-), IC1.16 (IN-), JP1.2, L2.P$1 (1), L3.P$1 (1), R1.1, R11.2, R27.2, T1.E, U1.6 (VBAT), U$12.4 (ILIM), U$12.8 (VIN)
VBAT_IN: IC1.1 (IN+), IC1.2 (IN+), IC1.3 (IN+), IC1.12 (VBUS), JP1.1, U16.P$1 (VOUT1), U16.P$20 (VOUT2)
VBAT_MEASURE: R11.1, R12.2; also elsewhere on the board
VBUS: C17.1, CHRG.A, CN4.VBUS, DONE.A, R13.1, R119.2, U16.P$3 (SEL), U16.P$4 (PROG2), U16.P$9 (/TE), U16.P$17 (CE), U16.P$18 (VIN1), U16.P$19 (VIN2)
VLIPO: B1.2 (+), C49.1, U16.P$14 (VBAT1), U16.P$15 (VBAT2), U16.P$16 (VBATSENS)

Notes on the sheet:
R2 < 500K R1 = 5.5*R2 (3.2V LBO)
Charging Circuitry
5V Regulation
6V Regulation (Motors)
Charge Rate = 1000V/PROG1
1.0K = 1000mA
2.0K = 500mA
No Thermistor:
10K NTC Thermistor:
RT1 = 0, RT2 = 10K
RT1 = TBD, RT2 = TBD
Both grounds must be connected on the PCB at only one point close to the GND pin.
On/Off Switch
See Pg 15 1st para
6.8uH power w/2A current
R3 = 1.9Mohm for 5.2V R3 = 1.1Mohm for 3.3V
Power Monitor

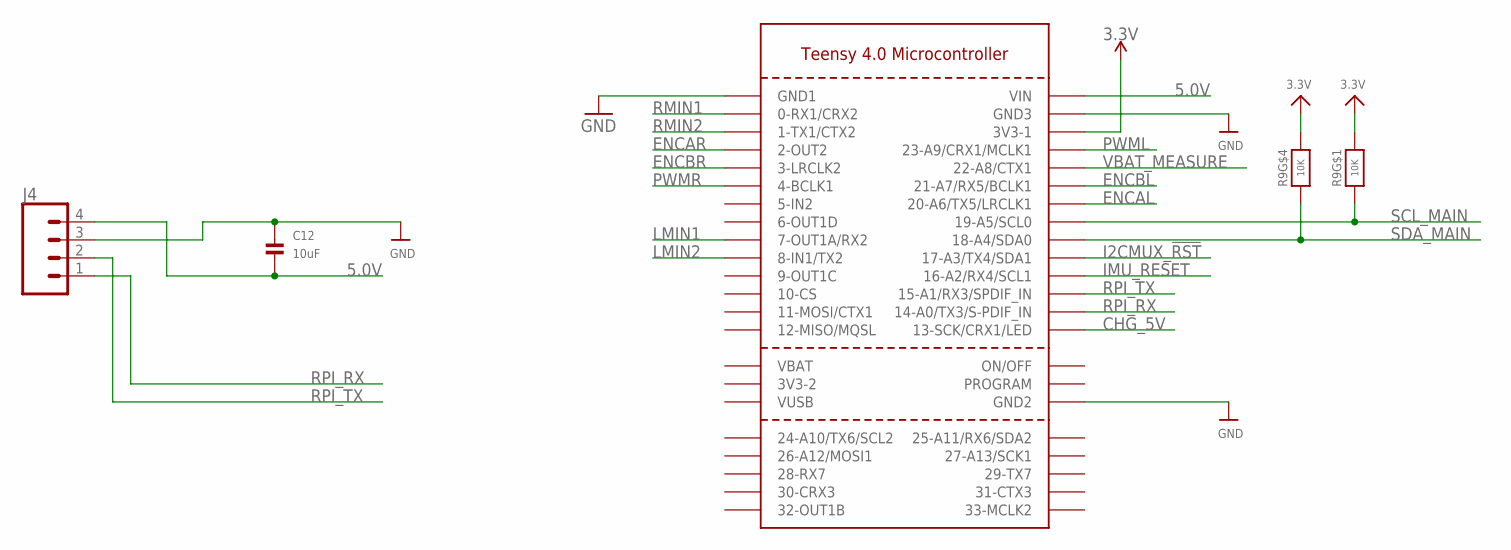
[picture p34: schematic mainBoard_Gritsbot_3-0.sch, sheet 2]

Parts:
C12: 10uF; 0603
J4: CONN_041X04_NO_SILK; 1X04_NO_SILK
R9: 10K; RESPACK_4X0603
U$57: TEENSY40

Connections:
3.3V: R9.1, R9.4 (1), U$57.3V3-1; also elsewhere on the board
5.0V: C12.2, J4.4, U$57.VIN; also elsewhere on the board
CHG_5V: U$57.13-SCK/CRX1/LED; also elsewhere on the board
ENCAL: U$57.20-A6/TX5/LRCLK1; also elsewhere on the board
ENCAR: U$57.2-OUT2; also elsewhere on the board
ENCBL: U$57.21-A7/RX5/BCLK1; also elsewhere on the board
ENCBR: U$57.3-LRCLK2; also elsewhere on the board
GND: C12.1, J4.3, U$57.GND1, U$57.GND2, U$57.GND3; also elsewhere on the board
I2CMUX_!RST: U$57.17-A3/TX4/SDA1; also elsewhere on the board
IMU_RESET: U$57.16-A2/RX4/SCL1; also elsewhere on the board
LMIN1: U$57.7-RX2/OUT1A (7-OUT1A/RX2); also elsewhere on the board
LMIN2: U$57.8-TX2/IN1 (8-IN1/TX2); also elsewhere on the board
PWML: U$57.23-A9/CRX1/CCLK1 (23-A9/CRX1/MCLK1); also elsewhere on the board
PWMR: U$57.4-BCLK2 (4-BCLK1); also elsewhere on the board
RMIN1: U$57.0-RX1 (0-RX1/CRX2); also elsewhere on the board
RMIN2: U$57.1-TX1 (1-TX1/CTX2); also elsewhere on the board
RPI_RX: J4.1, U$57.14-A0/TX3/S-PFI_OUT (14-A0/TX3/S-PDIF_IN)
RPI_TX: J4.2, U$57.15-A1/RX3/S-PDIF_IN (15-A1/RX3/SPDIF_IN)
SCL_MAIN: R9.8 (2), U$57.19-A5/SCL0; also elsewhere on the board
SDA_MAIN: R9.5 (2), U$57.18-A4/SDA0; also elsewhere on the board
VBAT_MEASURE: U$57.22-A8/CTX1; also elsewhere on the board

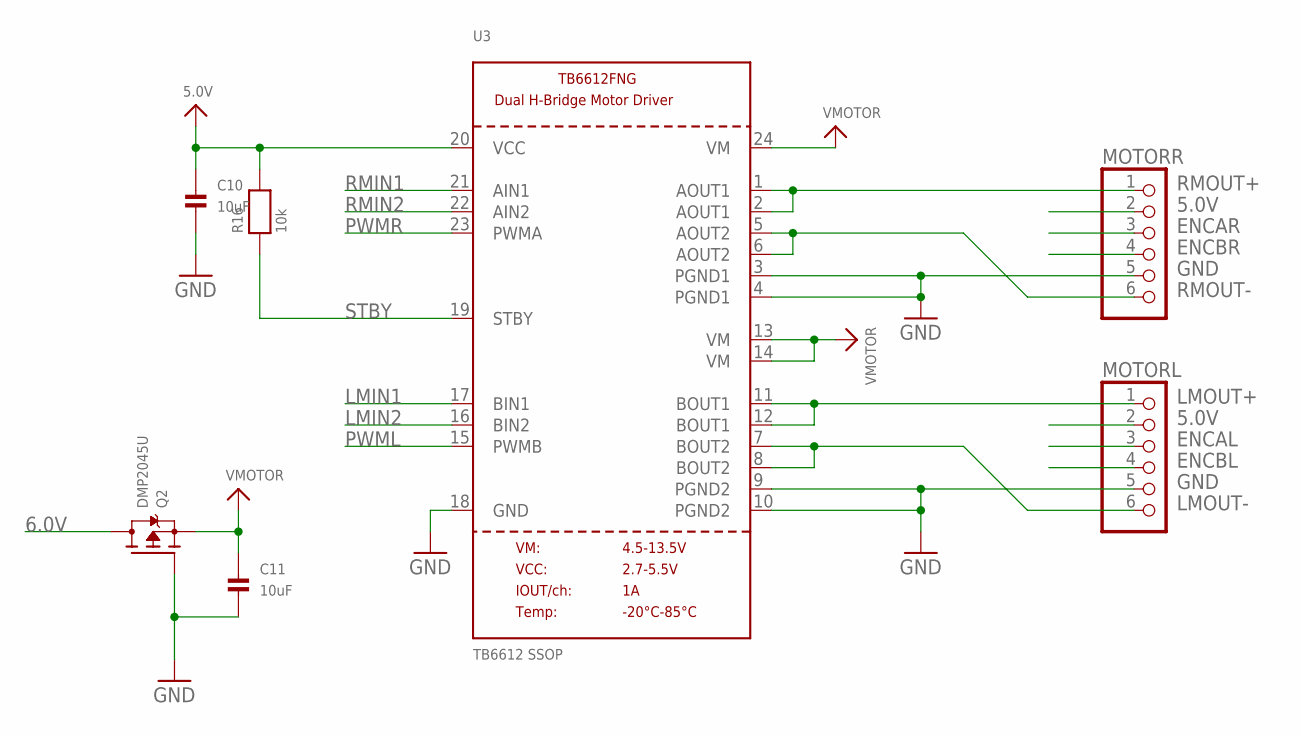
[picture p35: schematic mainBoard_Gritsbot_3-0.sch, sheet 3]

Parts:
C10, C11: 10uF; 0603
MOTORL: PINHD-1X6CB; 1X06-CLEANBIG
MOTORR: PINHD-1X6CB; 1X06-CLEANBIG
Q2: DMP2045U; SOT23-WIDE
R16: 10k; 0805
U3: TB6612 SSOP; SSOP24

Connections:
5.0V: C10.1, MOTORL.2, MOTORR.2, R16.2, U3.20 (VCC); also elsewhere on the board
6.0V: Q2.3 (D); also elsewhere on the board
ENCAL: MOTORL.3; also elsewhere on the board
ENCAR: MOTORR.3; also elsewhere on the board
ENCBL: MOTORL.4; also elsewhere on the board
ENCBR: MOTORR.4; also elsewhere on the board
GND: C10.2, C11.2, MOTORL.5, MOTORR.5, Q2.1 (G), U3.3 (PGND1), U3.4 (PGND1), U3.9 (PGND2), U3.10 (PGND2), U3.18 (GND); also elsewhere on the board
LMIN1: U3.17 (BIN1); also elsewhere on the board
LMIN2: U3.16 (BIN2); also elsewhere on the board
LMOUT+: MOTORL.1, U3.11 (BOUT1), U3.12 (BOUT1)
LMOUT-: MOTORL.6, U3.7 (BOUT2), U3.8 (BOUT2)
PWML: U3.15 (PWMB); also elsewhere on the board
PWMR: U3.23 (PWMA); also elsewhere on the board
RMIN1: U3.21 (AIN1); also elsewhere on the board
RMIN2: U3.22 (AIN2); also elsewhere on the board
RMOUT+: MOTORR.1, U3.1 (AOUT1), U3.2 (AOUT1)
RMOUT-: MOTORR.6, U3.5 (AOUT2), U3.6 (AOUT2)
STBY: R16.1, U3.19 (STBY)
VMOTOR: C11.1, Q2.2 (S), U3.13 (VM), U3.14 (VM), U3.24 (VM)

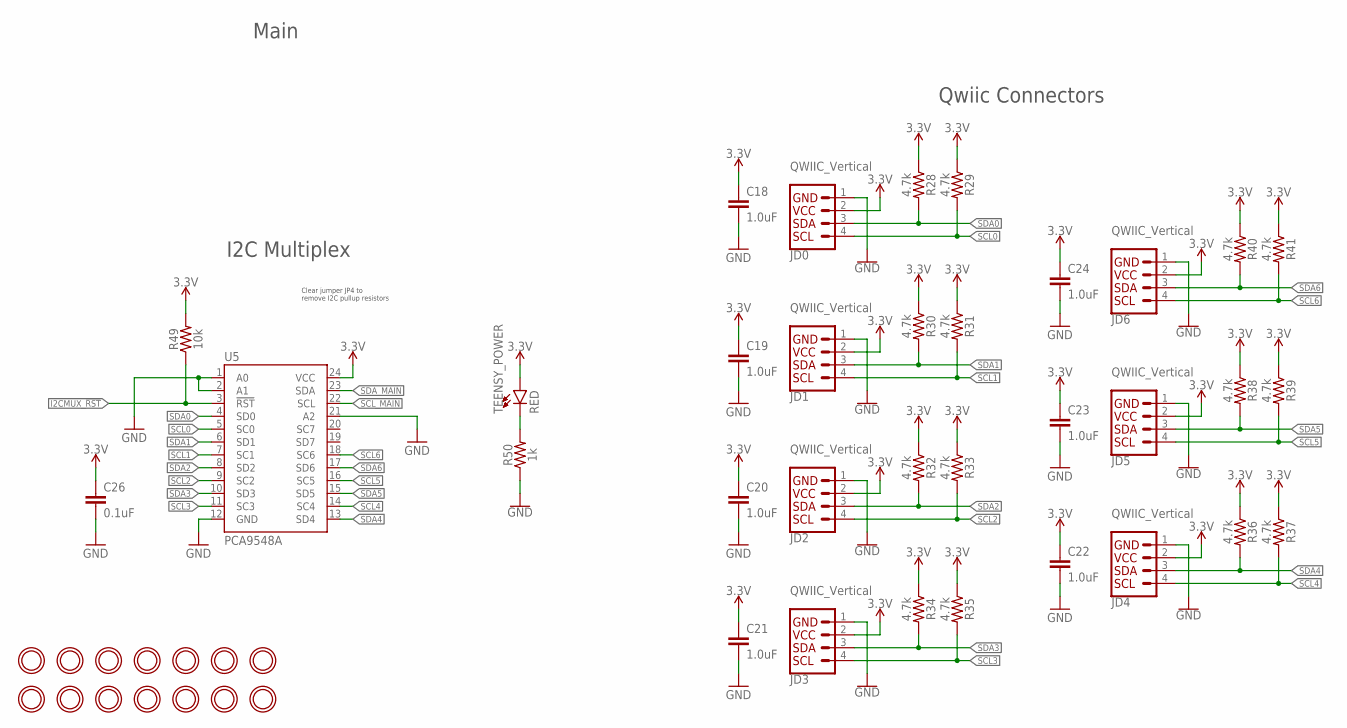
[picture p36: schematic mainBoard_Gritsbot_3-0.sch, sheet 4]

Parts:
C18, C19, C20, C21, C22, C23, C24: 1.0uF; 0603
C26: 0.1uF; 0603
JD0, JD1, JD2, JD3, JD4, JD5, JD6: QWIIC_Vertical; JST04_1MM_VERT
R28, R29, R30, R31, R32, R33, R34, R35, R36, R37, R38, R39, R40, R41: 4.7k; 0603
R49: 10k; 0603
R50: 1k; 0603
TEENSY_POWER: RED; LED-0603
U5: PCA9548A; TSSOP28
U$8, U$30, U$31, U$32, U$33, U$34, U$35, U$36, U$37, U$43, U$45, U$46, U$47, U$48: MOUNTINGHOLE2.5; MOUNTINGHOLE_2.5_PLATED

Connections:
3.3V: C18.1, C19.1, C20.1, C21.1, C22.1, C23.1, C24.1, C26.1, JD0.2, JD1.2, JD2.2, JD3.2, JD4.2, JD5.2, JD6.2, R28.1, R29.1, R30.1, R31.1, R32.1, R33.1, R34.1, R35.1, R36.1, R37.1, R38.1, R39.1, R40.1, R41.1, R49.2, TEENSY_POWER.A, U5.24 (VCC); also elsewhere on the board
GND: C18.2, C19.2, C20.2, C21.2, C22.2, C23.2, C24.2, C26.2, JD0.1, JD1.1, JD2.1, JD3.1, JD4.1, JD5.1, JD6.1, R50.1, U5.1 (A0), U5.2 (A1), U5.12 (GND), U5.21 (A2); also elsewhere on the board
I2CMUX_!RST: R49.1, U5.3 (!RST); also elsewhere on the board
unnamed: R50.2, TEENSY_POWER.C
SCL0: JD0.4, R29.2, U5.5 (SC0)
SCL1: JD1.4, R31.2, U5.7 (SC1)
SCL2: JD2.4, R33.2, U5.9 (SC2)
SCL3: JD3.4, R35.2, U5.11 (SC3)
SCL4: JD4.4, R37.2, U5.14 (SC4)
SCL5: JD5.4, R39.2, U5.16 (SC5)
SCL6: JD6.4, R41.2, U5.18 (SC6)
SCL_MAIN: U5.22 (SCL); also elsewhere on the board
SDA0: JD0.3, R28.2, U5.4 (SD0)
SDA1: JD1.3, R30.2, U5.6 (SD1)
SDA2: JD2.3, R32.2, U5.8 (SD2)
SDA3: JD3.3, R34.2, U5.10 (SD3)
SDA4: JD4.3, R36.2, U5.13 (SD4)
SDA5: JD5.3, R38.2, U5.15 (SD5)
SDA6: JD6.3, R40.2, U5.17 (SD6)
SDA_MAIN: U5.23 (SDA); also elsewhere on the board

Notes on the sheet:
Qwiic Connectors
Main
I2C Multiplex
Clear jumper JP4 to remove I2C pullup resistors

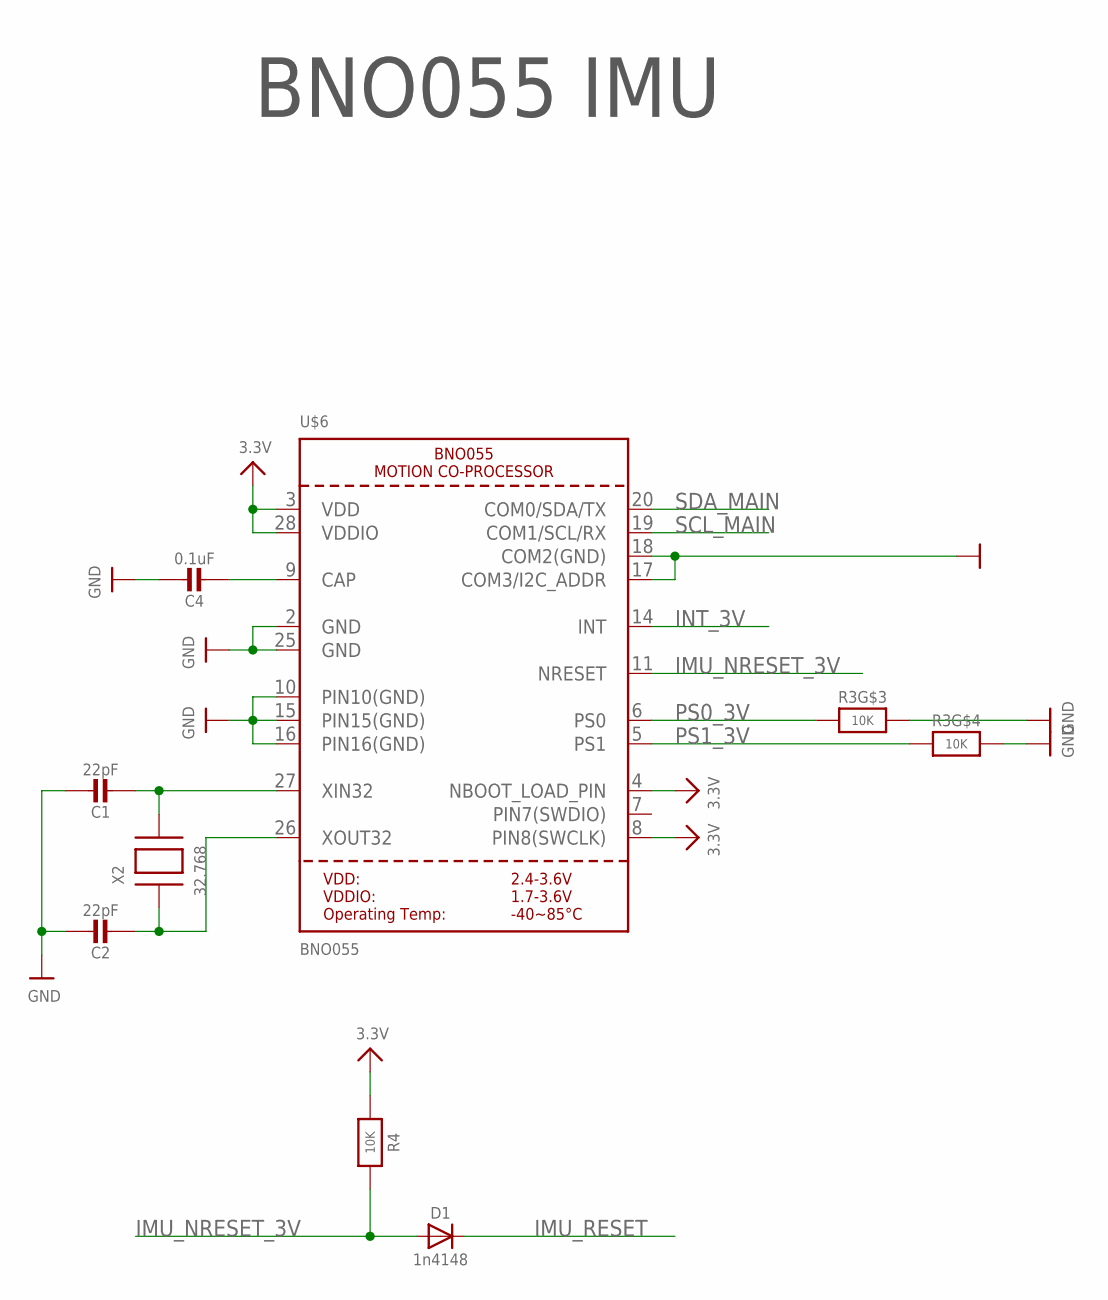
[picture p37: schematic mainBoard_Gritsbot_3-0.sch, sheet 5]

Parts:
C1, C2: 22pF; 0603-NO
C4: 0.1uF; 0603-NO
D1: 1n4148; SOD-323
R3: 10K; RESPACK_4X0603
R4: 10K; 0603-NO
U$6: BNO055
X2: 32.768; XTAL3215

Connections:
3.3V: R4.1, U$6.3 (VDD), U$6.4 (NBOOT_LOAD_PIN), U$6.8 (PIN8(SWCLK)), U$6.28 (VDDIO); also elsewhere on the board
GND: C1.1, C2.1, C4.1, R3.5 (2), R3.6 (2), U$6.2 (GND), U$6.10 (PIN10(GND)), U$6.15 (PIN15(GND)), U$6.16 (PIN16(GND)), U$6.17 (COM3/I2C_ADDR), U$6.18 (COM2(GND)), U$6.25 (GND); also elsewhere on the board
IMU_NRESET_3V: D1.A, R4.2, U$6.11 (NRESET)
IMU_RESET: D1.C; also elsewhere on the board
INT_3V: U$6.14 (INT)
unnamed: C1.2, U$6.27 (XIN32), X2.P$2
unnamed: C2.2, U$6.26 (XOUT32), X2.P$1
unnamed: C4.2, U$6.9 (CAP)
PS0_3V: R3.3 (1), U$6.6 (PS0)
PS1_3V: R3.4 (1), U$6.5 (PS1)
SCL_MAIN: U$6.19 (COM1/SCL/RX); also elsewhere on the board
SDA_MAIN: U$6.20 (COM0/SDA/TX); also elsewhere on the board

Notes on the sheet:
BNO055 IMU

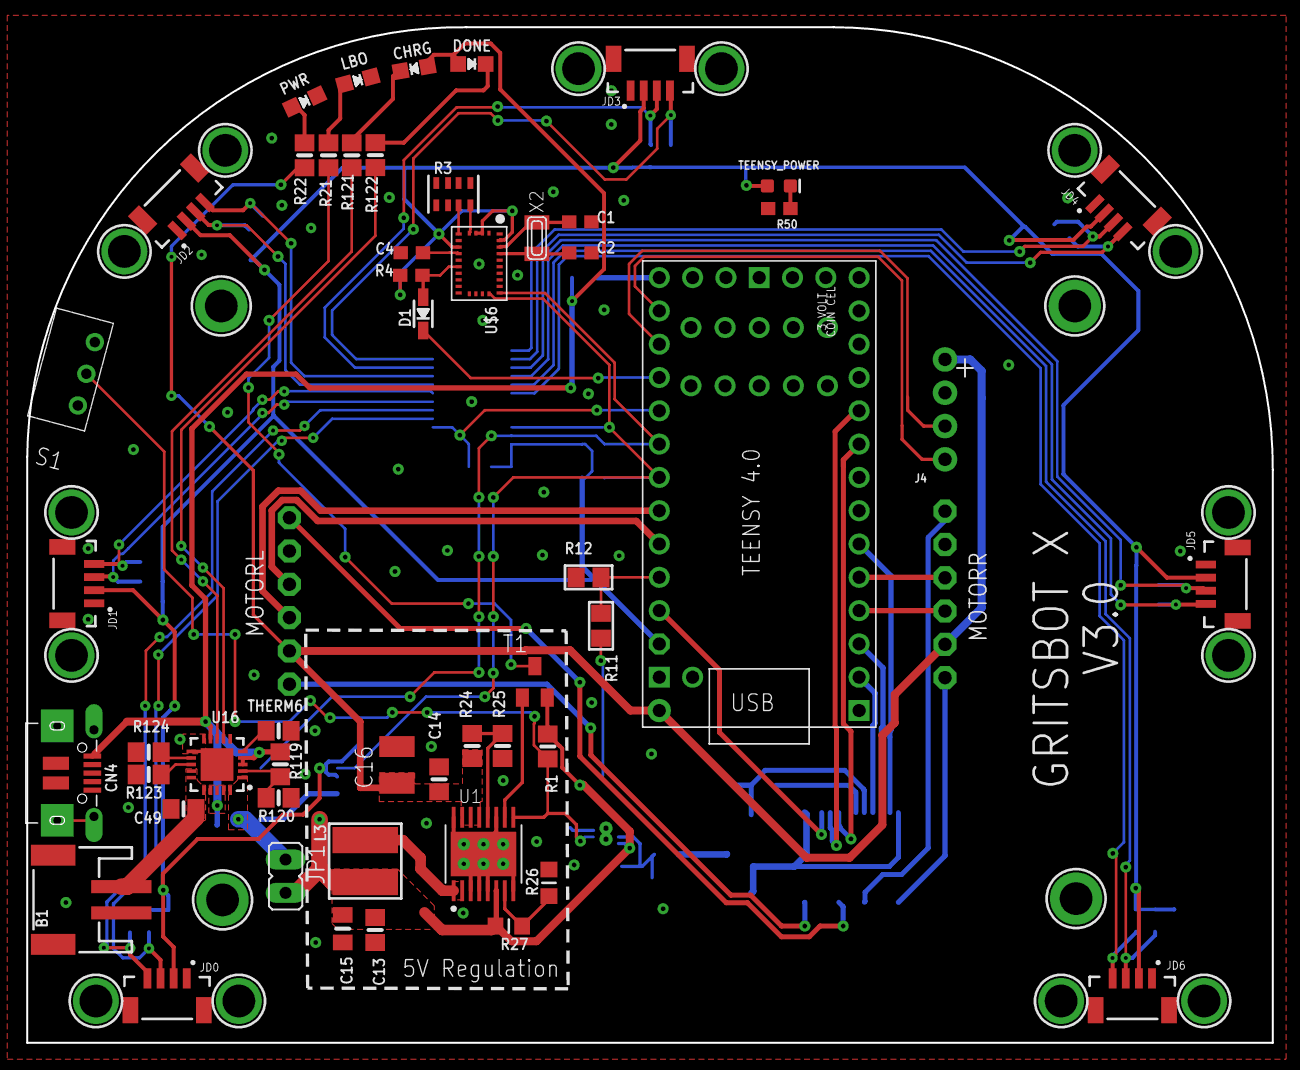
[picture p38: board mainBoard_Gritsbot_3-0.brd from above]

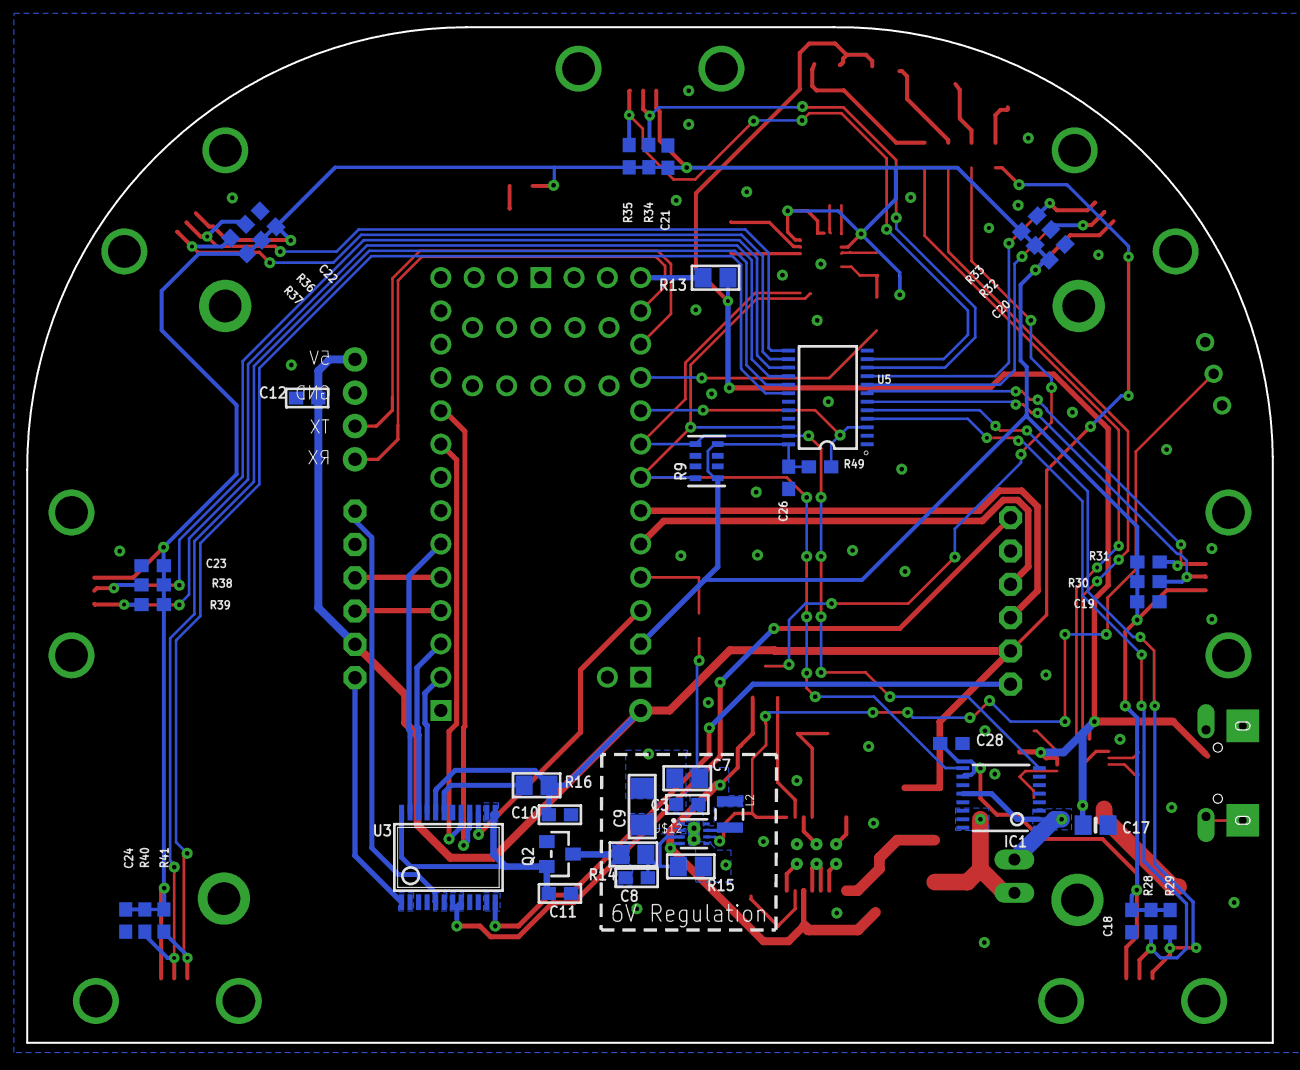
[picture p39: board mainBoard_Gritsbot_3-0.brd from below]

Board: 2 copper layers, 95.0 x 77.5 mm, 115 parts (43 on the bottom side), 71 nets.

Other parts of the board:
U$7, U$23, U$28, U$29: MOUNTINGHOLE_2.5_PLATED_THICK

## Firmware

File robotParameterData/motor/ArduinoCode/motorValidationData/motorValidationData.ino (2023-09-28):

// Determine the Motor Characteristics for GRITSBOTX 

// PIN DEFINITIONS 

// Motor A(left) and B(right) are connected to AIN1,AIN2 and BIN1 and BIN2 on the motor controller 

#include <Encoder.h>

//////DEFINE ENCODER OBJECTS FOR LEFT AND RIGHT WHEEL //////////////
Encoder motorLeft(5, 6);
Encoder motorRight(21,20);

//  Pin Definitions 
int STBY = 4; // motor driver enable 
int led = 13; // Teensy LED Pin 

// Motor A 
int PWMA = 9; // control the speed 
int AIN1 = 0; // direction 
int AIN2 = 1; // direction 

//Motor B 
int PWMB = 10; // speed control 
int BIN1 = 2; // direction 
int BIN2 = 3; // direction 


//Constants

float pi = 3.14159265359;

//Encoder Count Storage
int countR = 0; // Current count for RIGHT encoder.
int countL = 0; // Current count for LEFT encoder.

int oldCountR = 0;
int oldCountL = 0;

//Other Variables
float timeStart=0;
float timeStartStep=0;

float experimentTime = 60; //60 seconds.
float stepExperimentTime = 2000; // 2 Seconds in ms.

float samplingTime = 5; //10 ms sampling time.

//PID Stuff
float PIDMotorsTimeStart = 0;
float oldErrorL = 0;
float oldErrorR = 0;
float oldMotorPIDEncoderCountL = 0;
float oldMotorPIDEncoderCountR = 0;
float encoderCountsPerRotation = 12;
float motorGearRatio = 150.58;
float kpMotor = 6.01;
float kiMotor = 613;
float kdMotor = 0;
int motorL = 0;
int motorR = 0;

float desVel[5] = {random(-8,8), random(-8,8), random(-8,8), random(-8,8), random(-8,8)};//rad/s

int input = 0;

////////////////////// SETUP //////////////////////////////////
void setup() {
  // define the pins as outputs
  pinMode(STBY,OUTPUT);
  pinMode(led,OUTPUT);
  
  pinMode(PWMA,OUTPUT);
  pinMode(AIN1,OUTPUT);
  pinMode(AIN2,OUTPUT);

  pinMode(PWMB,OUTPUT);
  pinMode(BIN1,OUTPUT);
  pinMode(BIN2,OUTPUT);

  digitalWrite(led, LOW);    // turn the LED off by making the voltage LOW
  delay(1000);               // wait for a second

  Serial.begin(115200);

  while (!Serial) {
    ; // wait for serial port to connect. Needed for native USB
  }
  delay(1000);//Allow Time for Matlab to start.
  PIDMotorsTimeStart = millis();
}

//////////////// MAIN LOOP ////////////////////////////////////

void loop()                     
{ 
  for (int i = 0; i<5; i++){
    if (i == 0){
      timeStart = millis();
    }
    timeStartStep=millis();
    while (millis() - timeStartStep < stepExperimentTime){
      PIDMotorControl(desVel[i],desVel[i]);
      if (millis() - timeStart >= samplingTime){
        readEncoders();
        timeStart = millis();
        //Correct for wrap around
        if (countL < 0 && oldCountL > 0){
          countL = ((countL - (-2147483648)) + (2147483647 - oldCountL));
        }
        if (countR < 0 && oldCountR > 0){
          countR = ((countR - (-2147483648)) + (2147483647 - oldCountR)); // (rad)
        }
        oldCountR = countR;
        oldCountL = countL;
        Serial.print(int(countL));
        Serial.print(",");
        Serial.print(int(countR));
        Serial.print(",");
        Serial.print(int(millis()));
        Serial.print(",");
        Serial.println(desVel[i]);    
        Serial.flush();
       }
    }
  }
  

   stop();
   Serial.flush();
   Serial.print("Done");
   Serial.end();
   while(1){
      digitalWrite(led, HIGH);   // turn the LED on (HIGH is the voltage level)
      delay(1000);               // wait for a second
      digitalWrite(led, LOW);    // turn the LED off by making the voltage LOW
      delay(1000);               // wait for a second
   }
}
////////////////// FUNCTIONS //////////////////////////////////
void moveR(int motorSpeed){
  //Assume forward at first
  boolean in1 = HIGH;
  boolean in2 = LOW;

  //If motor speed is negative we want to rotate wheel backwards
  if (motorSpeed < 0){
     in1 = LOW;
     in2 = HIGH;
  }
   
  // Truncate PWM input to 255
  if (abs(motorSpeed)>255){
    motorSpeed = 255;
  }

  // Move the motor.
  digitalWrite(STBY, HIGH);
  digitalWrite(BIN1,in1);
  digitalWrite(BIN2,in2);
  analogWrite(PWMB, abs(motorSpeed)); 
}

void moveL(int motorSpeed){
  //Assume forward at first
  boolean in1 = LOW;
  boolean in2 = HIGH;

  //If motor speed is negative we want to rotate wheel backwards
  if (motorSpeed < 0){
     in1 = HIGH;
     in2 = LOW;
  }
   
  // Truncate PWM input to 255
  if (abs(motorSpeed)>255){
    motorSpeed = 255;
  }

  // Move the motor.
  digitalWrite(STBY, HIGH);
  digitalWrite(AIN1,in1);
  digitalWrite(AIN2,in2);
  analogWrite(PWMA, abs(motorSpeed));
}

void brake(){
  //Brakes the motors. (Locked to not rotate passively, this can be overcome by enough torque)
  digitalWrite(STBY, HIGH);
  
  analogWrite(PWMA, LOW);
  digitalWrite(AIN1, HIGH);
  digitalWrite(AIN2, HIGH);
  
  analogWrite(PWMB, LOW);
  digitalWrite(BIN1, HIGH);
  digitalWrite(BIN2, HIGH);
}

//Positive speed drives straight
void driveStraight(int motorSpeed){
  moveL(motorSpeed);
  moveR(motorSpeed);
}

//Positive speed turns right
void turn(int motorSpeed){
  moveL(motorSpeed);
  moveR(-motorSpeed);
}

void stop() {
  // Turns the motors off. (They can still rotate passively) 
  digitalWrite(STBY,LOW);
}

void readEncoders(){
  countR = -motorRight.read();
  countL = motorLeft.read();
}

void PIDMotorControl(float desLVel, float desRVel){
    /*Keeps the rotational speeds of the individual motors at setpoints desLVel and desRVel (rad/s).*/

    float timeStep = 10;

    if (millis() - PIDMotorsTimeStart >= timeStep){
      float PIDTimeStep = (millis() - PIDMotorsTimeStart)/1000;//Time step for controller to work on (s).

      readEncoders();

      // Error on individual motors for vel control
      float errorL = desLVel - 2 * pi * (countL - oldMotorPIDEncoderCountL) / (encoderCountsPerRotation * motorGearRatio * PIDTimeStep);
      float errorR = desRVel - 2 * pi * (countR - oldMotorPIDEncoderCountR) / (encoderCountsPerRotation * motorGearRatio * PIDTimeStep);
      float integralL = integralL + errorL * PIDTimeStep;
      float integralR = integralR + errorR * PIDTimeStep;
      float diffL = (oldErrorL - errorL) / PIDTimeStep;
      float diffR = (oldErrorR - errorR) / PIDTimeStep;
      oldErrorL = errorL;
      oldErrorR = errorR;
      oldMotorPIDEncoderCountL = countL;
      oldMotorPIDEncoderCountR = countR;

      motorL += int((kpMotor*errorL + kiMotor*integralL + kdMotor*diffL));
      motorR += int((kpMotor*errorR + kiMotor*integralR + kdMotor*diffR));

      moveL(motorL);
      moveR(motorR);
      
      PIDMotorsTimeStart = millis();
    }
}

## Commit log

2023-09-28 Moved from GTernal repository
    [Back Panel 3mm.obj, Battery Plate.obj, Bottom Panel.obj, Camera Mount V3.obj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]
2023-10-17 Updated files with the most recent iteration
    [BOM_GTernal.xlsx, GTernal Blown Out View v3.f3z, GTernal v30.f3z, Gritsbot_3.f3z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]
2024-04-28 Updated design files, documents, and BOM
    [BOM_GTernal.xlsx, Body1.obj, Body10.obj, Body11.obj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]
2024-04-29 Updated the laser cutting files for the top plates
2024-10-07 Updated the assembly section
2024-10-07 Added new files for lasercutting and motor PID tuning via MATLAB
2025-09-26 Updated the lasercutting files

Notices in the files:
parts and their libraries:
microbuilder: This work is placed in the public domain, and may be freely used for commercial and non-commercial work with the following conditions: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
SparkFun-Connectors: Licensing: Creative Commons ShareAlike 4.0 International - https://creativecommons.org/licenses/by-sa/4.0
